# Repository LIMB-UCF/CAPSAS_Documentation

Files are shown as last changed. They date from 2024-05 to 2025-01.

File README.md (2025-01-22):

# Common Arm Position Signal Acquisition System (CAPSAS)
#### *Created by the Laboratory for Interaction of Machine and Brain (LIMB) at the University of Central Florida*

## Introduction
Surface electromyography (sEMG) is the leading method of non-invasive control of prosthetic hands. Using sEMG recorded over a short time window, machine-learning algorithms can be used to classify intended hand gestures with high accuracy if the training and testing data are collected when the arm’s location remains relatively the same. However, during activities of daily living (ADL), the arm position varies, deteriorating gesture recognition accuracy. Therefore, to systematically study how arm position influences hand gesture recognition, we have built a device to position subjects’ arms at different locations across two dimensions while recording sEMG and upper limb kinematics using motion trackers. Compared to existing methods, the innovative device improves the data collection process for upper limb prosthesis experiments. Since the system is automated, datasets can be collected with minimal experimenter interference. Additionally, since the system is open source, other laboratories worldwide can build similar systems to create standardized datasets. Such datasets, collected across participants and days, will provide invaluable insights for robust myoelectric control of prosthetic hands invariant to the limb position.

## Explanation of the Project (Video)
https://youtu.be/4Bmu42mNIyQ

## Using the CAPSAS



The CAPSAS is composed of sixteen hexagons, each with twelve LEDs and an IR distance sensor in the middle. An Arduino Mega receives information from the computer about what LED animation to display at which location. Once received, it will then return a message whenever the IR sensor for that hexagon is triggered. You can learn more about the physical construction of the CAPSAS at this [link](https://github.com/LIMB-UCF/CAPSAS_Documentation/tree/main/CAPSAS%20Physical%20Parts). 

The sEMG of the forearm is recorded to the [Lab Streaming Layer](https://github.com/sccn/labstreaminglayer) (LSL). Additionally, kinematics of the trunk, arm, forearm, and wrist are recorded by four VIVE trackers. The IR sensor timestamps are currently recorded in a separate CSV to be interpreted in post-processing. You can learn more about the software of the CAPSAS at this [link](https://github.com/LIMB-UCF/CAPSAS_Documentation/tree/main/CAPSAS%20Code). 

The [material cost](https://github.com/LIMB-UCF/CAPSAS_Documentation/blob/main/CAPSAS%20Physical%20Parts/CAPSAS%20BOM.csv) of the CAPSAS is around $1000 USD, assuming access to a 3D printer and laser cutter. The EMG and kinematics data tracking are also not included in that price, but the LSL can be configured for other devices too. 

Don't want to build the CAPSAS but still want to use our dimensions? We created a [PDF poster](https://github.com/LIMB-UCF/CAPSAS_Documentation/blob/main/CAPSAS_Poster.pdf) of the CAPSAS for easy use!

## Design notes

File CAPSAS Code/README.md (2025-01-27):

## Overview
First, the computer will send an integer to the Arduino that codes for a specific animation and location. Then, once the IR is triggered, the Arduino will send a message to the Serial port. The Python code then marks when the IR is triggered and saves the data to a CSV file.

Simultaneously, a program on the computer will be recording sEMG and kinematic data of the arm. The sEMG armband used is an OyMotion gForcePro+, which collects eight data channels at 500 Hz. The arm kinematics are tracked using four VIVE VR motion trackers at 500 Hz. All data streams are synchronized and recorded using the Lab Streaming Layer Python library. 

## General Installation
SteamVR must be installed and configured. 

Additionally, Python must be installed with the required libraries: 
- numpy
- pylsl 
- pynput
- colorama
- pybullet
- threading_module
- triad_openvr
- asyncio
- struct
- contextlib
- dataclasses 
- bleak 

## General Use

Three python files must be run in the following order:

`python oymotion_streamer.py`

This starts the EMG stream.

`python imu_stream.py`

This starts the IMU data stream. A live view of the trackers is also provided.

`python event_marker.py`

This starts to communicate with the Arduino. 

***Finally, you must start recording the data within the LSL GUI.***

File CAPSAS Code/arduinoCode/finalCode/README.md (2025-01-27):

Open all three files in Arduino IDE, then upload the "serialplusLED.ino" to the board.
 
- serialplusLED.ino is the main file with logic for the experiment.
- LEDfun.ino contains functions for the LED animations.
- serialStuff.ino contains processing code for the serial communication between the computer and Arduino.

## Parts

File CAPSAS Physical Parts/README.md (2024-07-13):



***Figure 1:** CAPSAS Dimensions and Frame*

The general structure of the CAPSAS is provided in Figure 1. Seven 36” and two 72” pieces of 1.5” square aluminum tubing are connected with metal brackets and 3D-printed parts to form the basis for which everything else is mounted. The 72” aluminum tubing was purchased with holes every 1 ½”, which is useful for the height adjustability of the system. Two pieces of the 36” tubing are used to form the base of the system and a 3D-printed [part](https://github.com/LIMB-UCF/CAPSAS_Documentation/blob/main/CAPSAS%20Physical%20Parts/STLs/Frame%20%26%20Hexagon%20Related%20Items/wheel%20cap%20v3.stl) is used to connect 4” casters to the tubing. Next, four [1.5” metal T brackets](https://www.amazon.com/dp/B0B34HG1YD/) were used to connect the vertical 72” tubing. Additionally, 3D-printed brackets were used for the [bottom](https://github.com/LIMB-UCF/CAPSAS_Documentation/blob/main/CAPSAS%20Physical%20Parts/STLs/Frame%20%26%20Hexagon%20Related%20Items/t%20connector%20v4.stl) and [top](https://github.com/LIMB-UCF/CAPSAS_Documentation/blob/main/CAPSAS%20Physical%20Parts/STLs/Frame%20%26%20Hexagon%20Related%20Items/top%20elbow%20v3.stl) horizontal pieces of 36” aluminum to form the frame. Finally, an H-shaped piece of aluminum can be prepared by cutting two pieces of 36” aluminum in half and connecting them 9” away from the ends of another 36” piece with [brackets](https://www.amazon.com/Riuog-Brackets-Patterned-Bracket-Furniture/dp/B0B7N1QT6Z/). The H-shaped piece of aluminum holds the hexagons on the front of the CAPSAS through the blue brackets seen in Figure 1. The brackets were created in [three different sizes](https://github.com/LIMB-UCF/CAPSAS_Documentation/tree/main/CAPSAS%20Physical%20Parts/STLs/Frame%20%26%20Hexagon%20Related%20Items/Frame%20to%20Hexagon) to fit the hexagons to the front of the CAPSAS. It is connected to the metal frame through the height adjustment mechanism, seen in green in Figure 1.



***Figure 2:** Height Adjustment Mechanism*

The height adjustment mechanism was central to the CAPSAS because it allows our lab to collect data from various heights based on the shoulder height of the individual. A detailed look at the height adjustment mechanism is provided in Figure 2. It is composed of [several 3D-printed parts](https://github.com/LIMB-UCF/CAPSAS_Documentation/tree/main/CAPSAS%20Physical%20Parts/STLs/Frame%20%26%20Hexagon%20Related%20Items/Height%20Adjustment%20Mechanism) as well as a [spring](https://www.amazon.com/uxcell-Diameter-Stainless-Extended-Compressed/dp/B07MP9TDSH/) and [metal rod](https://www.amazon.com/YXQ-M6x180mm-Double-Adjustable-Stainless/dp/B07QPCWPXQ/) in each cylinder. An animation of the motion is also available in [this video](https://youtu.be/rhj-_HMj1IY).



***Figure 3:** Hexagon Layout*

All sixteen hexagons are constructed similarly to the one in Figure 3 using [laser cutting](https://github.com/LIMB-UCF/CAPSAS_Documentation/tree/main/CAPSAS%20Physical%20Parts/DXFs) (we laser cut acrylic but later had to cover the shiny surface with matte paper due to reflection issues with the VIVE motion trackers). Each has 12 addressable RGB LEDs constructed by soldering four pieces of 3 LEDs cut from a [30 LED per meter strip](https://www.amazon.com/SEZO-Individually-Addressable-Programmable-Non-Waterproof/dp/B097BX7P3V/) (as seen in brown in Figure 3). The order in which the LEDs are soldered is essential, as the controller calls them sequentially. Each hexagon has its own power wires due to the heavy power draw if all 192 LEDs were lit simultaneously, but the DIN comes from the DOUT of the previous hexagon. Also, each has an IR distance sensor (center of Figure 3) with its power wires and data out wire that goes back to the Arduino I/O (Figure 4). The red [part](https://github.com/LIMB-UCF/CAPSAS_Documentation/blob/main/CAPSAS%20Physical%20Parts/STLs/Objects%20%26%20Holders/new%20magnet%20back%20v3.stl) at the center of Figure 3 is two Halbach arrays of [square neodymium magnets](https://www.amazon.com/LOVIMAG-Neodymium-Magnets-Whiteboard-Science/dp/B0CP1N6432/). Such an array of powerful magnets is necessary to ensure the participant does not accidentally knock off any [object holders](https://github.com/LIMB-UCF/CAPSAS_Documentation/tree/main/CAPSAS%20Physical%20Parts/STLs/Objects%20%26%20Holders) on the front of the hexagon. The light blue, rounded rectangles in Figure 3 are [3D-printed parts](https://github.com/LIMB-UCF/CAPSAS_Documentation/blob/main/CAPSAS%20Physical%20Parts/STLs/Frame%20%26%20Hexagon%20Related%20Items/Frame%20to%20Hexagon/connector%20block%20v2.stl) that connect the hexagon to the brackets seen in Figure 1. Heat press inserts were used so the parts could easily be screwed into the frame. Finally, [diffusers](https://github.com/LIMB-UCF/CAPSAS_Documentation/blob/main/CAPSAS%20Physical%20Parts/STLs/Frame%20%26%20Hexagon%20Related%20Items/light%20diffuse%20v2.stl) were 3D-printed from white PLA to reduce the intensity of the LED light.



***Figure 4:** Arduino and Wiring*

All 16 hexagons are connected to an Arduino Mega. Additionally, due to the potential high-power demands of the LEDs and the sheer number of wires, two pairs of [power rails](https://www.amazon.com/Positions-Terminal-Pre-Insulated-Barrier-MILAPEAK/dp/B07CLW5FPS/) must be used to power the hexagons. The power rails and Arduino are mounted to the aluminum frame behind the hexagons using [3D-printed parts](https://github.com/LIMB-UCF/CAPSAS_Documentation/tree/main/CAPSAS%20Physical%20Parts/STLs/Frame%20%26%20Hexagon%20Related%20Items/Arduino%20Mount%20to%20Frame). Finally, a [12 V](https://www.amazon.com/R-Tech-UL-Listed-Switching-Supply-Adapter/dp/B00FEOB4EI/) and [5 V](https://www.amazon.com/JOVNO-Converter-100-240V-Transformer-5-5x2-5mm/dp/B08764XJ2M/) power supply are used to input the power for the Arduino and LEDs, respectively. The power supplies are then secured to one of the vertical pieces of aluminum.

A bill of materials (BOM) can be found in this folder. The estimated cost of building the CAPSAS is $1000 USD, assuming a 3D printer and common tools are available. The cost can be reduced if a laser cutter is available as well. Finally, the whole system also requires 4 VIVE motion trackers (around $500 USD) and an OyMotion gForcePro+ EMG armband (around $2800 USD).

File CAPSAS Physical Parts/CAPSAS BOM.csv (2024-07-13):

Part | Price | Number | Total Price | Link
36" tubing, no holes | $20.43 | 4 | $81.72 | https://www.amazon.com/80-20-Smooth-Square-Profile/dp/B00J4SCV6U?ref_=ast_sto_dp&th=1
36" tubing, with holes | $22.95 | 3 | $68.85 | https://www.amazon.com/80-20-Smooth-Square-Profile/dp/B00J4SW764?ref_=ast_sto_dp
72" tubing, with holes | $43.11 | 2 | $86.22 | https://www.amazon.com/80-20-Smooth-Square-Profile/dp/B00J4SZOZ0?ref_=ast_sto_dp
4 inch casters (set of 4) | $26.99 | 1 | $26.99 | https://www.amazon.com/PRITEK-Replacement-Industrial-Trailer-Furniture/dp/B07423NB6K?cv_ct_cx=4%2Binch%2Bcaster%2Bwheels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
T-brackets set | $39.99 | 1 | $39.99 | https://www.amazon.com/dp/B0B34HG1YD/?th=1
Small metal brackets set | $18.99 | 1 | $18.99 | https://www.amazon.com/Riuog-Brackets-Patterned-Bracket-Furniture/dp/B0B7N1QT6Z/?th=1
Springs (set of 10) | $8.59 | 1 | $8.59 | https://www.amazon.com/uxcell-Diameter-Stainless-Extended-Compressed/dp/B07MP9TDSH/
M6 metal rod (set of 6) | $7.49 | 1 | $7.49 | https://www.amazon.com/YXQ-M6x180mm-Double-Adjustable-Stainless/dp/B07QPCWPXQ/?th=1
WS2812B LED light strip (30 LEDs/m) | $13.99 | 2 | $27.98 | https://www.amazon.com/SEZO-Individually-Addressable-Programmable-Non-Waterproof/dp/B097BX7P3V/?th=1
Square magnets (set of 50) | $13.99 | 5 | $69.95 | https://www.amazon.com/LOVIMAG-Neodymium-Magnets-Whiteboard-Science/dp/B0CP1N6432/
IR distance sensor (set of 10) | $8.79 | 2 | $17.58 | https://www.amazon.com/HiLetgo-Infrared-Avoidance-Reflective-Photoelectric/dp/B07W97H2WS
Power rails (set of 5) | $12.99 | 1 | $12.99 | https://www.amazon.com/Positions-Terminal-Pre-Insulated-Barrier-MILAPEAK/dp/B07CLW5FPS/?th=1
Arduino Mega | $20.99 | 1 | $20.99 | https://www.amazon.com/ELEGOO-ATmega2560-ATMEGA16U2-Arduino-Compliant/dp/B01H4ZDYCE
12 V power to Arduino | $18.99 | 1 | $18.99 | https://www.amazon.com/R-Tech-UL-Listed-Switching-Supply-Adapter/dp/B00FEOB4EI/?th=1
5 V power to LEDs | $22.99 | 1 | $22.99 | https://www.amazon.com/JOVNO-Converter-100-240V-Transformer-5-5x2-5mm/dp/B08764XJ2M/?th=1
Approximations:
Various metric nuts and bolts, heat inserts | $50 | 1 | $50.00
3D printing filament (~3 kg?) | $80 |  | $80
Laser cutting (online service) | $300 |  | $300
Wires, solder, etc. | $50 |  | $50
Epoxy (set of 2) | $14.98 | 2 | $29.96 | https://www.amazon.com/J-B-Weld-Plastic-Bonder-Syringe/dp/B0B5VJZ5XW
CAPSAS Total |  |  | $1,040.27

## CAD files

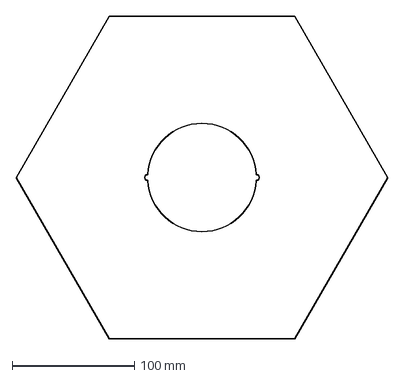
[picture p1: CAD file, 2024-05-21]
CAPSAS Physical Parts/DXFs/button hexagon.dxf
304.8 x 264.0 mm

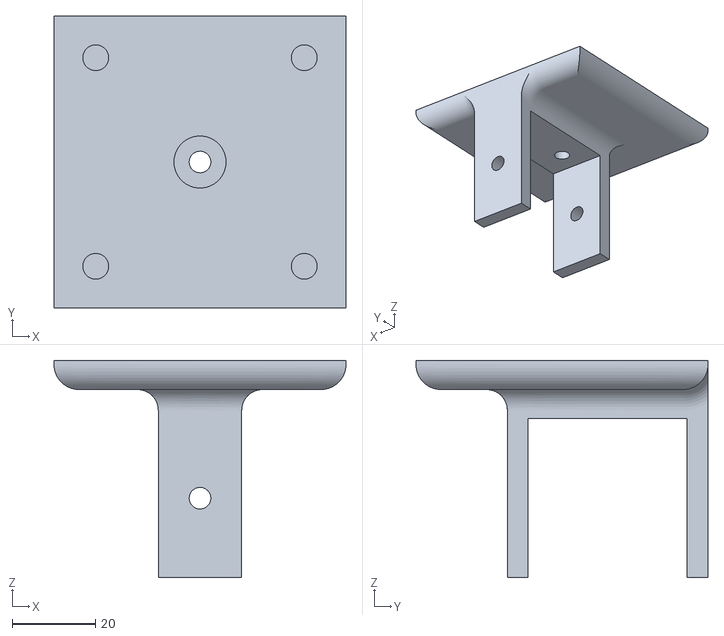
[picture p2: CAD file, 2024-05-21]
CAPSAS Physical Parts/STLs/Frame & Hexagon Related Items/Arduino Mount to Frame/arduino mount v1.stl
70.0 x 70.0 x 52.1

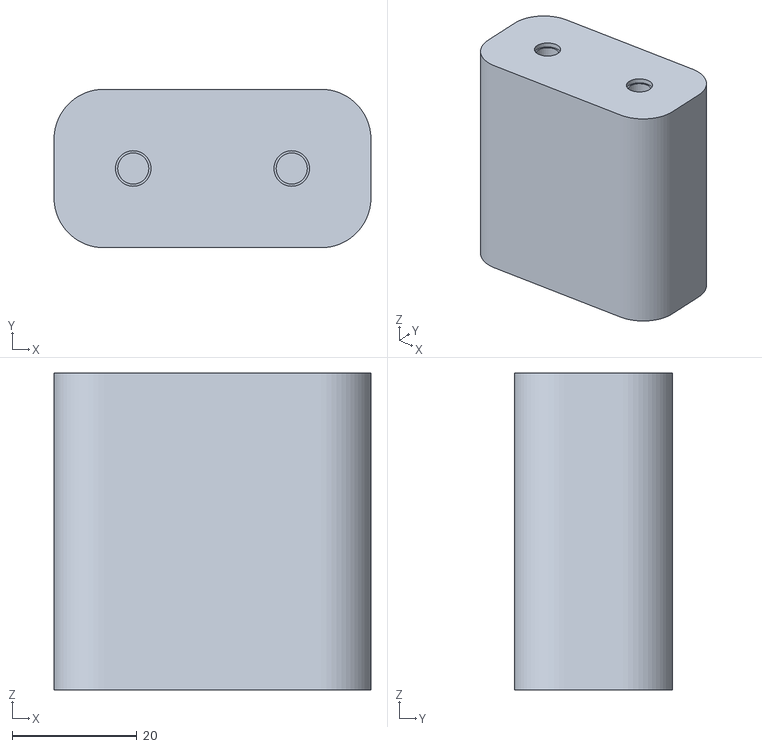
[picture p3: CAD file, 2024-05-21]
CAPSAS Physical Parts/STLs/Frame & Hexagon Related Items/Frame to Hexagon/connector block v2.stl
50.8 x 25.4 x 50.8

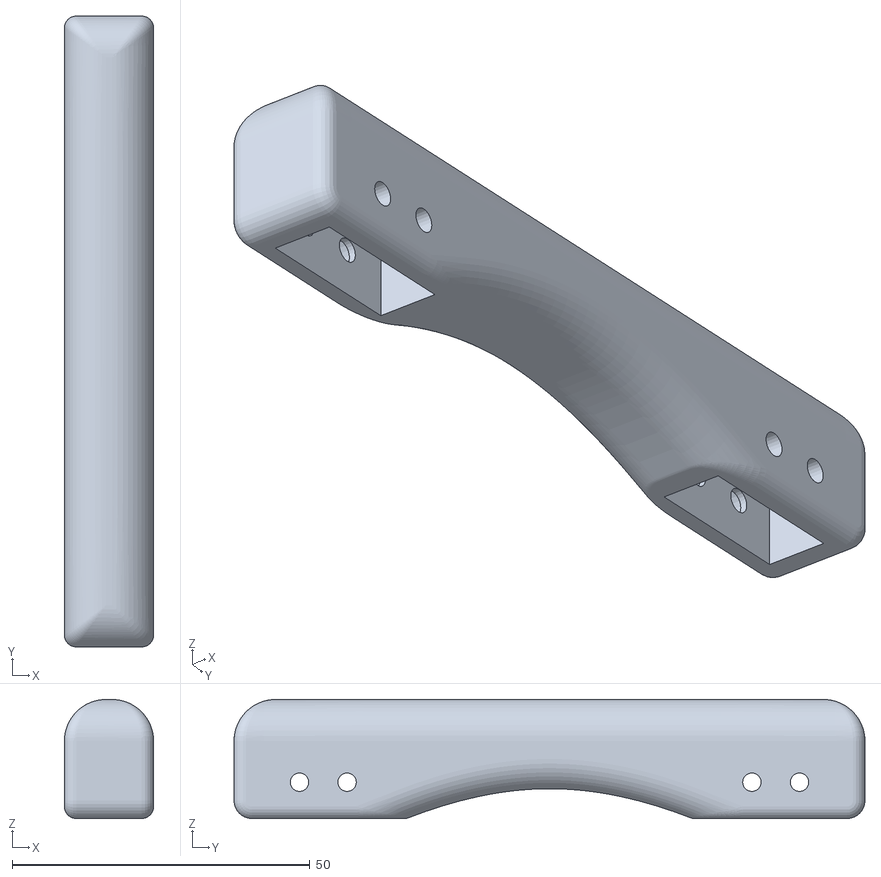
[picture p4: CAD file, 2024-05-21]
CAPSAS Physical Parts/STLs/Frame & Hexagon Related Items/Height Adjustment Mechanism/connector bar v2.stl
15.0 x 106.0 x 20.0

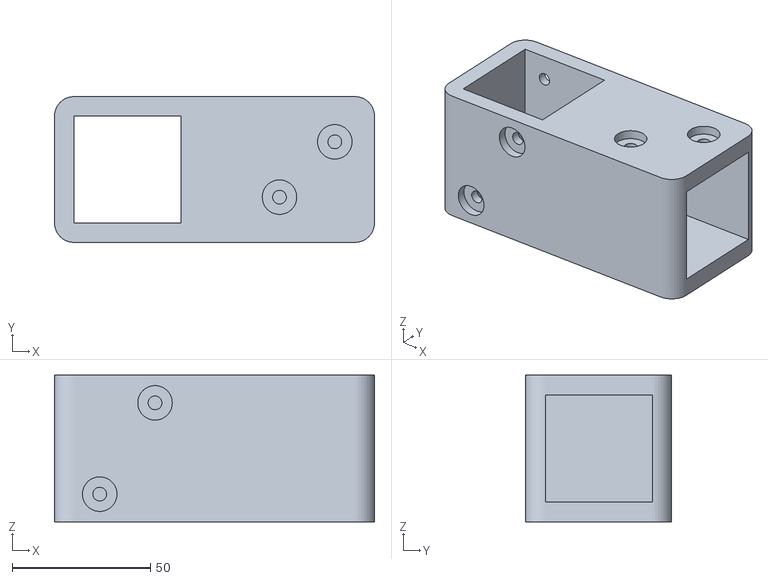
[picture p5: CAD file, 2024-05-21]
CAPSAS Physical Parts/STLs/Frame & Hexagon Related Items/t connector v4.stl
115.7 x 52.7 x 53.0

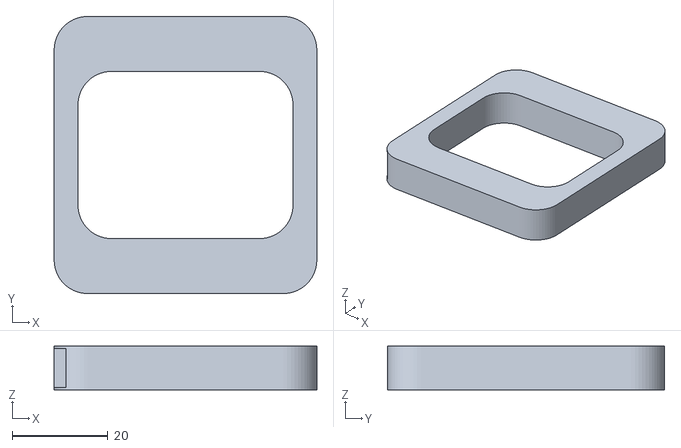
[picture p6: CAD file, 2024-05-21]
CAPSAS Physical Parts/STLs/Objects & Holders/new magnet back v3.stl
55.0 x 58.0 x 9.20

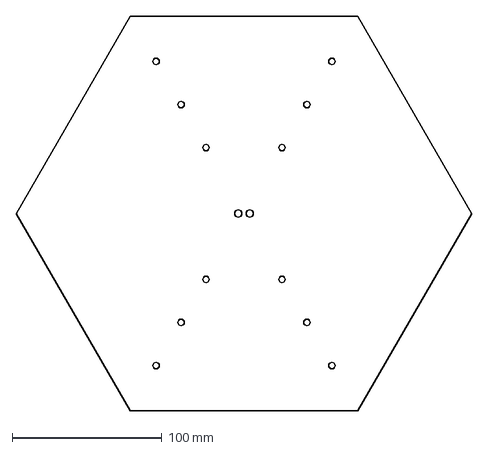
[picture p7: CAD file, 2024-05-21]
CAPSAS Physical Parts/DXFs/final led hex.dxf
304.8 x 264.0 mm

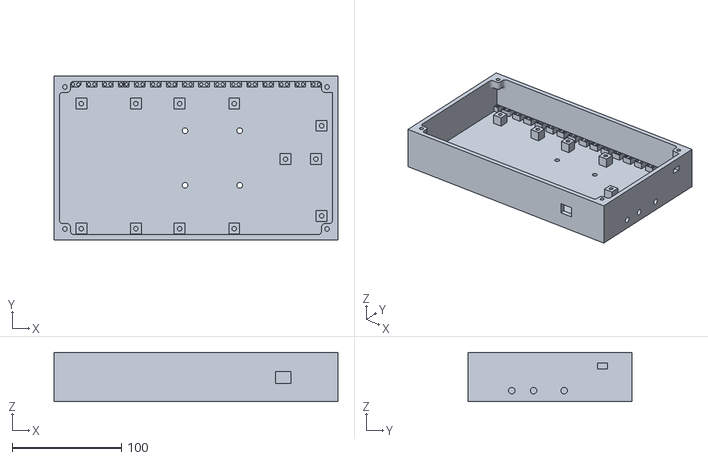
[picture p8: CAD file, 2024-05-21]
CAPSAS Physical Parts/STLs/Frame & Hexagon Related Items/Arduino Mount to Frame/arduino box v2.stl
260.0 x 150.0 x 45.0

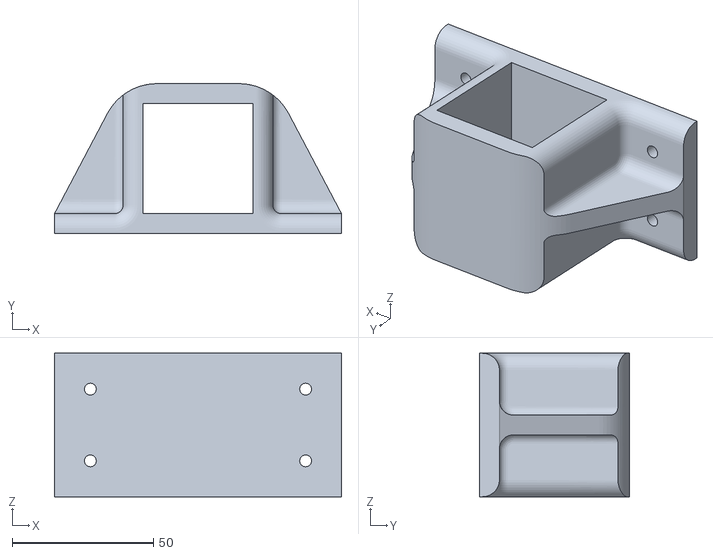
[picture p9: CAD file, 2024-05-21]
CAPSAS Physical Parts/STLs/Frame & Hexagon Related Items/Frame to Hexagon/tiny arms v1.stl
101.6 x 53.0 x 50.8

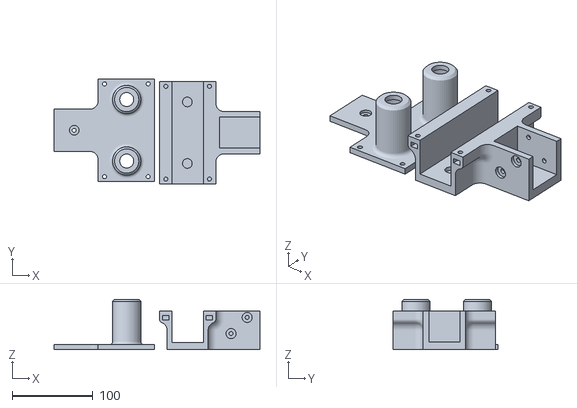
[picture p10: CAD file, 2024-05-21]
CAPSAS Physical Parts/STLs/Frame & Hexagon Related Items/Height Adjustment Mechanism/height adjust v14.stl
255.2 x 130.0 x 62.5

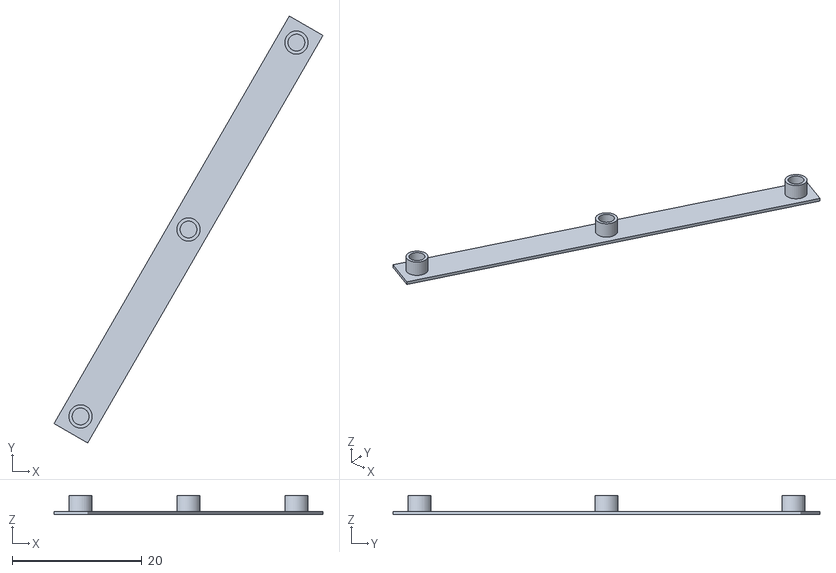
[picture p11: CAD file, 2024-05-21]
CAPSAS Physical Parts/STLs/Frame & Hexagon Related Items/light diffuse v2.stl
41.5 x 65.9 x 3.00

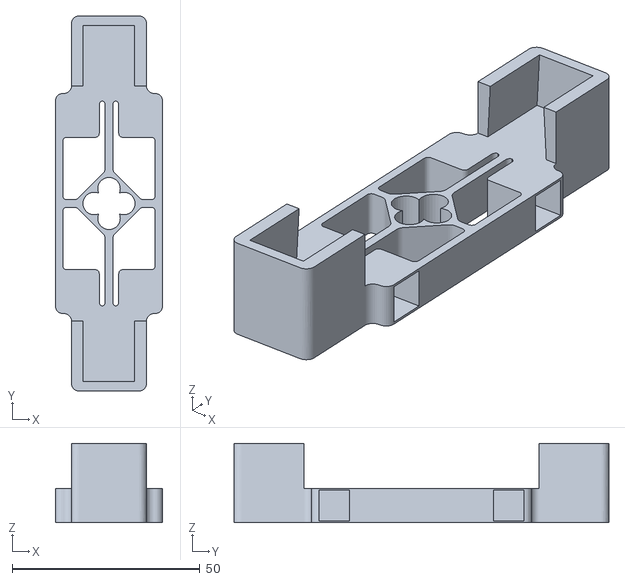
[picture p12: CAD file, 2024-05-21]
CAPSAS Physical Parts/STLs/Objects & Holders/new pen v2.stl
28.6 x 100.0 x 21.2

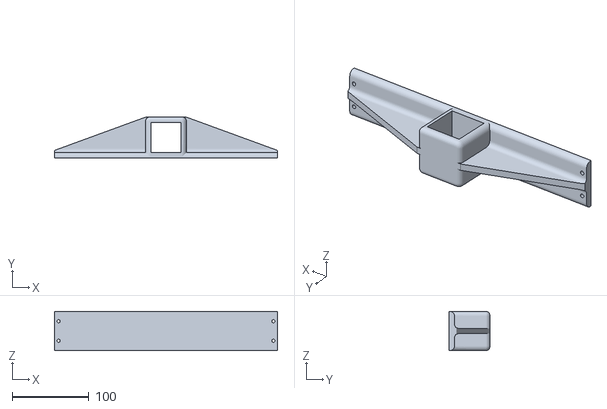
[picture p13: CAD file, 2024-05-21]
CAPSAS Physical Parts/STLs/Frame & Hexagon Related Items/Frame to Hexagon/large arms v5.stl
290.0 x 53.0 x 50.8

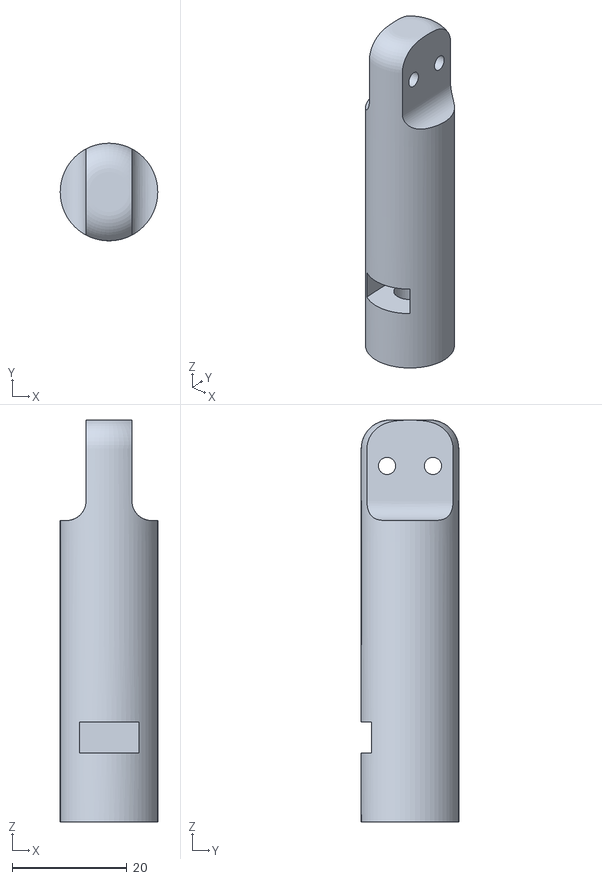
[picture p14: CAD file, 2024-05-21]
CAPSAS Physical Parts/STLs/Frame & Hexagon Related Items/Height Adjustment Mechanism/height adjust pin end v13.stl
17.0 x 17.0 x 70.0

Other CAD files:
CAPSAS Physical Parts/STLs/Frame & Hexagon Related Items/top elbow mirrored v2.stl
CAPSAS Physical Parts/STLs/Objects & Holders/new cup v7.stl
CAPSAS Physical Parts/STLs/Frame & Hexagon Related Items/Frame to Hexagon/small arms v3.stl
CAPSAS Physical Parts/STLs/Frame & Hexagon Related Items/top elbow v3.stl
CAPSAS Physical Parts/STLs/Frame & Hexagon Related Items/Height Adjustment Mechanism/height adjust washer v3.stl
CAPSAS Physical Parts/STLs/Frame & Hexagon Related Items/button fix v1.stl
CAPSAS Physical Parts/STLs/Frame & Hexagon Related Items/wheel cap v3.stl
CAPSAS Physical Parts/STLs/Objects & Holders/new card v3.stl
CAPSAS Physical Parts/STLs/Objects & Holders/new coin v2.stl
CAPSAS Physical Parts/STLs/Objects & Holders/objects v4.stl
CAPSAS Physical Parts/STLs/Prototype & Old STLs/arduino box v1.stl
CAPSAS Physical Parts/STLs/Prototype & Old STLs/card holder v1.stl
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

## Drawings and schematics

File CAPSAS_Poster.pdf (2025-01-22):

2

6

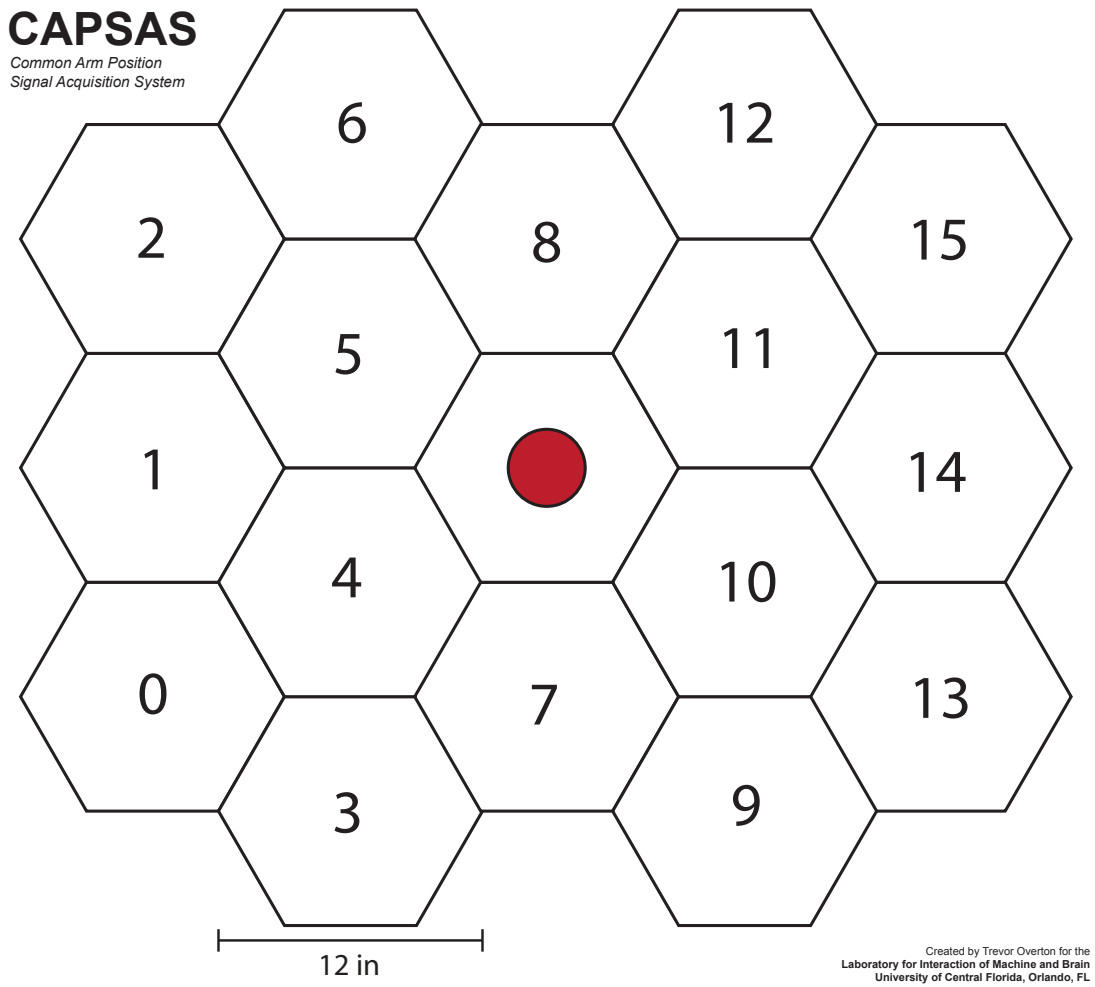
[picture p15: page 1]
CAPSAS

Common Arm Position
Signal Acquisition System

Created by Trevor Overton for the

Laboratory for Interaction of Machine and Brain
University of Central Florida, Orlando, FL

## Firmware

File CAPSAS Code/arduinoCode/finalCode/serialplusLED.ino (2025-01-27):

#include <Adafruit_NeoPixel.h>

#define PIN 10
#define NUMPIXELS 192
#define speed 1000

Adafruit_NeoPixel pixels(NUMPIXELS, PIN, NEO_GRB + NEO_KHZ800);

const byte numChars = 32;
char receivedChars[numChars];   // an array to store the received data
unsigned long previousMillis = 0UL;
unsigned long interval = 15UL;

int irState = HIGH;

bool newData = false;
unsigned int dataNumber = 0;

unsigned int curani = 65535;
unsigned long startMillis = millis();
bool trig = false;
bool dytrig = false;
bool rundynamic = false;
bool finishdynamic = false;
bool dyobjtrig = true;
bool v = true;
unsigned int curstartani = 0;

unsigned long dynamicmillis = 0;

unsigned int wait = 65535;

unsigned int hexnum = 0;
unsigned int aninum = 0;
unsigned int targetnum = 0;

char ca = 'a';
char IME = 'b';

unsigned long b = 0;
unsigned long c = 0;

byte byte1 = 0;
byte byte2 = 0;

void setup() {
  //open serial
  Serial.begin(115200);
  //start LEDs
  pixels.begin(); 
  //ready inputs
  pinMode(22, INPUT);
  pinMode(23, INPUT);
  pinMode(24, INPUT);
  pinMode(25, INPUT);
  pinMode(26, INPUT);
  pinMode(27, INPUT);
  pinMode(28, INPUT);
  pinMode(29, INPUT);
  pinMode(30, INPUT);
  pinMode(31, INPUT);
  pinMode(32, INPUT);
  pinMode(33, INPUT);
  pinMode(34, INPUT);
  pinMode(35, INPUT);
  pinMode(36, INPUT);
  pinMode(37, INPUT);
  pinMode(38, INPUT_PULLUP);

  while (v) {
    recvWithEndMarker();
    wait = showNewNumber();

    if (wait < 65535) {
      Serial.println(millis());
      //Serial.println(millis());
      v = false;
    }
  }
}

void loop() {
  recvWithEndMarker();
  unsigned int newani = (unsigned int)showNewNumber();
  unsigned long currentMillis = millis();
  
  if (newani < 65535) {
    curani = newani;
    //Serial.println(newani);
    startMillis = millis();
    pixels.clear();
    pixels.show();
    if ((curani >> 15) == 0) {
      hexnum = curani/5;
      aninum = curani%5;
      ca = 'b';
      IME = 'a';
    } else if ((curani >> 15) == 1) {
      curstartani = (curani >> 8) - 128;
      hexnum = curstartani/6;
      aninum = curstartani%6;
      targetnum = (curani & 0b0000000011111111)/6;
      ca = 'c';
      IME = 'a';
    }
  }
  //Serial.print(IME);
  switch (ca) {
    case 'b':
      switch (IME) {
        case 'a':
          if (hexnum == 16) {
            if (button(hexnum + 22)) {
              IME = 'b';
              break;
            }
          } else if (aninum == 0) {
            if (button(hexnum + 22)) {
              IME = 'b';
              break;
            }
            open(hexnum, startMillis);
          } else if (aninum == 1) {
            if (button(hexnum + 22)) {
              IME = 'b';
              break;
            }
            close(hexnum, startMillis);
          } else if (aninum == 2) {
            if (button(hexnum + 22)) {
              IME = 'b';
              break;
            }
            left(hexnum, startMillis);
          } else if (aninum == 3) {
            if (button(hexnum + 22)) {
              IME = 'b';
              break;
            }
            right(hexnum, startMillis);
          } else if (aninum == 4) {
            if (button(hexnum + 22)) {
              IME = 'b';
              break;
            }
            resi(hexnum, startMillis);
          }
          break;
        case 'b': 
          Serial.println(millis());
          int i = 250;
          if (hexnum < 16) {
            pixels.setPixelColor((hexnum*12) + 0, pixels.Color(0, i, 0));
            pixels.setPixelColor((hexnum*12) + 1, pixels.Color(0, i, 0));
            pixels.setPixelColor((hexnum*12) + 2, pixels.Color(0, i, 0));
            pixels.setPixelColor((hexnum*12) + 3, pixels.Color(0, i, 0));
            pixels.setPixelColor((hexnum*12) + 4, pixels.Color(0, i, 0));
            pixels.setPixelColor((hexnum*12) + 5, pixels.Color(0, i, 0));
            pixels.setPixelColor((hexnum*12) + 6, pixels.Color(0, i, 0));
            pixels.setPixelColor((hexnum*12) + 7, pixels.Color(0, i, 0));
            pixels.setPixelColor((hexnum*12) + 8, pixels.Color(0, i, 0));
            pixels.setPixelColor((hexnum*12) + 9, pixels.Color(0, i, 0));
            pixels.setPixelColor((hexnum*12) + 10, pixels.Color(0, i, 0));
            pixels.setPixelColor((hexnum*12) + 11, pixels.Color(0, i, 0));
            pixels.show();
            delay(wait*1000);
          }
          pixels.clear();
          Serial.println(millis());
          pixels.show();
          ca = 'a';
          IME = 'a';
          curani = 65535;
      }
      break;
    case 'c': //dynamic ********************************************************
      switch (IME) {
        case 'a':
          if (aninum == 0) {
              if (button(hexnum + 22)) {
                IME = 'b';
                cool(hexnum);
                dynamicmillis = millis();
                break;
              }
              open(hexnum, startMillis);
          } else if (aninum == 1) {
              if (button(hexnum + 22)) {
                IME = 'b';
                cool(hexnum);
                dynamicmillis = millis();
                break;
              }
              close(hexnum, startMillis);
          } else if (aninum == 2) {
              if (button(hexnum + 22)) {
                IME = 'b';
                cool(hexnum);
                dynamicmillis = millis();
                break;
              }
              left(hexnum, startMillis);
          } else if (aninum == 3) {
              if (button(hexnum + 22)) {
                IME = 'b';
                cool(hexnum);
                dynamicmillis = millis();
                break;
              }
              right(hexnum, startMillis);
          } else if (aninum == 4) {
              if (button(hexnum + 22)) {
                IME = 'b';
                cool(hexnum);
                dynamicmillis = millis();
                break;
              }
              resi(hexnum, startMillis);
          } else if (aninum == 5) {
              if (obbutton(hexnum + 22)) {
                IME = 'b';
                cool(hexnum);
                dynamicmillis = millis();
                break;
              }
              resi(hexnum, startMillis);
          }
          break;
        case 'b': 
          //Serial.println('hello');
          b = (millis() - dynamicmillis)/12; //12 for 3s
          //Serial.println(b);
          if (b > 250) {
            if (aninum < 5) {
              IME = 'c';
            } else if (aninum == 5) {
              IME = 'd';
            }
            break;
          } else {
            pixels.fill(pixels.Color(b,250-b,0), 0, 0); //change???
          }
          if (aninum == 0) {
              open(targetnum, startMillis);
          } else if (aninum == 1) {
              close(targetnum, startMillis);
          } else if (aninum == 2) {
              left(targetnum, startMillis);
          } else if (aninum == 3) {
              right(targetnum, startMillis);
          } else if (aninum == 4) {
              resi(targetnum, startMillis);
          } else if (aninum == 5) {
              resi(targetnum, startMillis);
          }
          break;
        case 'c':
          c = millis() - dynamicmillis; 
          if (c%500 < 250) {
            pixels.fill(pixels.Color(250,0,0), 0, 0); 
          } else {
            pixels.clear();
          }
          if (aninum == 0) {
              if (button(targetnum + 22)) {
                IME = 'd';
                break;
              }
              open(targetnum, startMillis);
          } else if (aninum == 1) {
              if (button(targetnum + 22)) {
                IME = 'd';
                break;
              }
              close(targetnum, startMillis);
          } else if (aninum == 2) {
              if (button(targetnum + 22)) {
                IME = 'd';
                break;
              }
              left(targetnum, startMillis);
          } else if (aninum == 3) {
              if (button(targetnum + 22)) {
                IME = 'd';
                break;
              }
              right(targetnum, startMillis);
          } else if (aninum == 4) {
              if (button(targetnum + 22)) {
                IME = 'd';
                break;
              }
              resi(targetnum, startMillis);
          } else if (aninum == 5) {
              if (button(targetnum + 22)) {
                Serial.println(millis());
                ca = 'a';
                IME = 'a';
                b = 0;
                c = 0;
                pixels.clear();
                pixels.show();
                curani = 65535;
                break;
              }
              resi(targetnum, startMillis);
          }
          break;
        case 'd':
          if (aninum < 5) {
            Serial.println(millis());
          }
          pixels.clear();
          pixels.setPixelColor((targetnum*12) + 0, pixels.Color(0, 250, 0));
          pixels.setPixelColor((targetnum*12) + 1, pixels.Color(0, 250, 0));
          pixels.setPixelColor((targetnum*12) + 2, pixels.Color(0, 250, 0));
          pixels.setPixelColor((targetnum*12) + 3, pixels.Color(0, 250, 0));
          pixels.setPixelColor((targetnum*12) + 4, pixels.Color(0, 250, 0));
          pixels.setPixelColor((targetnum*12) + 5, pixels.Color(0, 250, 0));
          pixels.setPixelColor((targetnum*12) + 6, pixels.Color(0, 250, 0));
          pixels.setPixelColor((targetnum*12) + 7, pixels.Color(0, 250, 0));
          pixels.setPixelColor((targetnum*12) + 8, pixels.Color(0, 250, 0));
          pixels.setPixelColor((targetnum*12) + 9, pixels.Color(0, 250, 0));
          pixels.setPixelColor((targetnum*12) + 10, pixels.Color(0, 250, 0));
          pixels.setPixelColor((targetnum*12) + 11, pixels.Color(0, 250, 0));
          pixels.show();
          delay(3000);
          pixels.clear();
          pixels.show();
          if (aninum == 5) {
            dynamicmillis = millis();
            IME = 'c';
          } else {
            ca = 'a';
            IME = 'a';
            b = 0;
            curani = 65535;
          }
      }
      break;
    default:
      //waiting for new serial
      break;
  }

  if(currentMillis - previousMillis > interval) {
    pixels.show();
    previousMillis = currentMillis;
  }
}

bool button(int irPin) {
  irState = digitalRead(irPin);
  bool triggered = false; //should be false
  if (irState == LOW) { //change  to LOW
    triggered = true;
  }
  return triggered;
}

bool obbutton(int irPin) {
  irState = digitalRead(irPin);
  bool triggered = false;
  if (irState == HIGH) { 
    triggered = true;
  }
  return triggered;
}

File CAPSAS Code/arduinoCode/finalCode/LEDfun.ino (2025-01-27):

void close(int hex, unsigned long startms) {
  unsigned long currentMillis = millis();

    unsigned long b = millis() - startms;
    unsigned long c = b%750;
    int i = 0; 

    if (c < 250) {
      i = c;
      pixels.setPixelColor((hex*12) + 0, pixels.Color(0, i, i));
      pixels.setPixelColor((hex*12) + 5, pixels.Color(0, i, i));
      pixels.setPixelColor((hex*12) + 6, pixels.Color(0, i, i));
      pixels.setPixelColor((hex*12) + 11, pixels.Color(0, i, i));
      pixels.setPixelColor((hex*12) + 1, pixels.Color(0, 0, 0));
      pixels.setPixelColor((hex*12) + 4, pixels.Color(0, 0, 0));
      pixels.setPixelColor((hex*12) + 7, pixels.Color(0, 0, 0));
      pixels.setPixelColor((hex*12) + 10, pixels.Color(0, 0, 0));
      pixels.setPixelColor((hex*12) + 2, pixels.Color(0, 0, 0));
      pixels.setPixelColor((hex*12) + 3, pixels.Color(0, 0, 0));
      pixels.setPixelColor((hex*12) + 8, pixels.Color(0, 0, 0));
      pixels.setPixelColor((hex*12) + 9, pixels.Color(0, 0, 0));
      //pixels.show();
    }
    else if (c < 500) {
      i = c - 250;
      pixels.setPixelColor((hex*12) + 0, pixels.Color(0, 250 - i, 250 - i));
      pixels.setPixelColor((hex*12) + 5, pixels.Color(0, 250 - i, 250 - i));
      pixels.setPixelColor((hex*12) + 6, pixels.Color(0, 250 - i, 250 - i));
      pixels.setPixelColor((hex*12) + 11, pixels.Color(0, 250 - i, 250 - i));
      pixels.setPixelColor((hex*12) + 1, pixels.Color(0, i, i));
      pixels.setPixelColor((hex*12) + 4, pixels.Color(0, i, i));
      pixels.setPixelColor((hex*12) + 7, pixels.Color(0, i, i));
      pixels.setPixelColor((hex*12) + 10, pixels.Color(0, i, i));
      pixels.setPixelColor((hex*12) + 2, pixels.Color(0, 0, 0));
      pixels.setPixelColor((hex*12) + 3, pixels.Color(0, 0, 0));
      pixels.setPixelColor((hex*12) + 8, pixels.Color(0, 0, 0));
      pixels.setPixelColor((hex*12) + 9, pixels.Color(0, 0, 0));
      //pixels.show();
    }
    else if (c < 750) {
      i = c - 500;
      pixels.setPixelColor((hex*12) + 1, pixels.Color(0, 250 - i, 250 - i));
      pixels.setPixelColor((hex*12) + 4, pixels.Color(0, 250 - i, 250 - i));
      pixels.setPixelColor((hex*12) + 7, pixels.Color(0, 250 - i, 250 - i));
      pixels.setPixelColor((hex*12) + 10, pixels.Color(0, 250 - i, 250 - i));
      pixels.setPixelColor((hex*12) + 2, pixels.Color(0, i, i));
      pixels.setPixelColor((hex*12) + 3, pixels.Color(0, i, i));
      pixels.setPixelColor((hex*12) + 8, pixels.Color(0, i, i));
      pixels.setPixelColor((hex*12) + 9, pixels.Color(0, i, i));
      pixels.setPixelColor((hex*12) + 0, pixels.Color(0, 0, 0));
      pixels.setPixelColor((hex*12) + 5, pixels.Color(0, 0, 0));
      pixels.setPixelColor((hex*12) + 6, pixels.Color(0, 0, 0));
      pixels.setPixelColor((hex*12) + 11, pixels.Color(0, 0, 0));
      //pixels.show();
    }

}

void resi(int hex, unsigned long startms) {
  unsigned long currentMillis = millis();
    int i = 250;
    pixels.setPixelColor((hex*12) + 0, pixels.Color(0, i, i));
    pixels.setPixelColor((hex*12) + 1, pixels.Color(0, i, i));
    pixels.setPixelColor((hex*12) + 2, pixels.Color(0, i, i));
    pixels.setPixelColor((hex*12) + 3, pixels.Color(0, i, i));
    pixels.setPixelColor((hex*12) + 4, pixels.Color(0, i, i));
    pixels.setPixelColor((hex*12) + 5, pixels.Color(0, i, i));
    pixels.setPixelColor((hex*12) + 6, pixels.Color(0, i, i));
    pixels.setPixelColor((hex*12) + 7, pixels.Color(0, i, i));
    pixels.setPixelColor((hex*12) + 8, pixels.Color(0, i, i));
    pixels.setPixelColor((hex*12) + 9, pixels.Color(0, i, i));
    pixels.setPixelColor((hex*12) + 10, pixels.Color(0, i, i));
    pixels.setPixelColor((hex*12) + 11, pixels.Color(0, i, i));
    //pixels.show();
}
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

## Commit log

2024-05-21 adding code
    [arduino box v1.stl, arduino box v2.stl, arduino mount v1.stl, button fix v1.stl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]
2024-05-25 added folder
    [connector bar v2.stl, connector block v2.stl, large arms v5.stl, small arms v3.stl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]
2024-07-13 Added bill of materials
    [CAPSAS BOM.csv]
2024-07-13 Update README.md w/ bill of materials
2024-07-13 Update README.md with bill of materials
